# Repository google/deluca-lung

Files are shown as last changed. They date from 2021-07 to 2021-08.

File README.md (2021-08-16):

# deluca-lung

## Getting started
Instructions to provide to students: run the following commands
```
pip install deluca-lung
jupyter notebook
```

Navigate to the notebook `demo/2021-07-18 controller demo.ipynb` and run the cells.

## Setting up Raspberry Pi
- Create a Raspberry Pi OS image via [this](https://github.com/MinRegret/rpi-gadget-image-creator)

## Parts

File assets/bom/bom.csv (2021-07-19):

Category | Component | Quantity | Units / Package | $ / Package | # of Packages | Subtotal | Shipping | Tax | Total | Per Vent | Supplier | Link | Notes
Electronics | PCB for sensor / solenoid driver | 1 | 5 | $20.30 | 1 | $20.30 |  |  | $20.30 | $4.06 | JLCPCB | https://jlcpcb.com | https://github.com/MinRegret/deluca-lung/tree/main/assets/pcb/venti-zero
Electronics | Raspberry Pi Zero | 1 | 1 | $10.00 | 1 | $10.00 |  |  | $10.00 | $10.00 | Adafruit | https://www.adafruit.com/product/3400
Electronics | GPIO header | 1 | 1 | $0.95 | 1 | $0.95 |  |  | $0.95 | $0.95 | Adafruit | https://www.adafruit.com/product/2822
Electronics | GPIO ribbon | 1 | 1 | $2.50 | 1 | $2.50 |  |  | $2.50 | $2.50 | Mouser | https://www.mouser.com/ProductDetail/SparkFun/CAB-13028?qs=sGAEpiMZZMtyU1cDF2RqUE5bpLI3XpN5e3FkFOusz3o%3D
Electronics | 120W 24V Power Supply | 1 | 1 | $35.29 | 1 | $35.29 |  |  | $35.29 | $35.29 | Mouser | https://www.mouser.com/ProductDetail/709-RPS-120S-24
Electronics | 2-pin 5.08mm PCB screw terminal | 2 | 1 | $0.93 | 2 | $1.86 |  |  | $1.86 | $1.86 | Mouser | https://www.mouser.com/ProductDetail/571-2828372
Electronics | Female quick disconnct terminal | 3 | 1 | $0.30 | 3 | $0.90 |  |  | $0.90 | $0.90 | Mouser | https://www.mouser.com/ProductDetail/TE-Connectivity/3-520125-2?qs=%252BHUO%252BPuWh%2Fq0sCGvvzeevQ%3D%3D
Electronics | Pressure sensor | 1 | 1 | $42.00 | 1 | $42.00 |  |  | $42.00 | $42.00 | Mouser | https://www.mouser.com/ProductDetail/683-1PSI-D1-4V-MINI
Electronics | Flow sensor | 1 | 1 | $52.70 | 1 | $52.70 |  |  | $52.70 | $52.70 | Mouser | https://www.mouser.com/ProductDetail/683-5INCH-D2-P4VMINI
Electronics | MicroSD card | 1 | 1 | $7.99 | 1 | $7.99 |  |  | $7.99 | $7.99 | Mouser | https://www.mouser.com/ProductDetail/Parallax/32328?qs=%252BEew9%252B0nqrBvH%252BuscVQRmA%3D%3D
Electronics | 16 AWG wire | 0.5 | 200 | $16.95 | 1 | $16.95 |  |  | $16.95 | $0.04 | Amazon | https://www.amazon.com/GS-Power-Aluminum-Speaker-Amplifier/dp/B07584SQX5?s=electronics
Electronics | AC power inlet | 1 | 1 | $15.15 | 1 | $15.15 |  |  | $15.15 | $15.15 | McMaster | https://www.mcmaster.com/5428N114/
Electronics | Mini HDMI to HDMI extension cable | 1 | 1 | $17.50 | 1 | $17.50 |  |  | $17.50 | $17.50 | Amazon | https://www.amazon.com/gp/product/B075LH8K3W/ref=ppx_yo_dt_b_asin_title_o00_s00?ie=UTF8&th=1
Electronics | MicroSD extension cable | 1 | 1 | $5.99 | 1 | $5.99 |  |  | $5.99 | $5.99 | Amazon | https://www.amazon.com/gp/product/B07WWVBK8V/ref=ppx_yo_dt_b_search_asin_title?ie=UTF8&psc=1
Electronics | Micro USB extension cable | 1 | 2 | $5.99 | 1 | $5.99 |  |  | $5.99 | $3.00 | Amazon | https://www.amazon.com/gp/product/B07YDG6B6R/ref=ppx_yo_dt_b_asin_title_o00_s01?ie=UTF8&psc=1
Pneumatics | Inspiratory valve | 1 | 1 | $107.10 | 1 | $107.10 |  |  | $107.10 | $107.10 | SMC Pneumatics | https://www.smcpneumatics.com/PVQ31-5G-23-01N-H.html
Pneumatics | Expiratory valve | 1 | 1 | $58.80 | 1 | $58.80 |  |  | $58.80 | $58.80 | SMC Pneumatics | https://www.smcpneumatics.com/VXZ230EF.html
Pneumatics | Inspiratory right angle connector | 1 | 2 | $0.01 | 1 | $0.01 |  |  | $0.01 | $0.01 | TO PRINT | https://github.com/MinRegret/deluca-lung/blob/main/assets/stl/inspiratory-right-angle%20v4.stl
Pneumatics | Expiratory right angle connector | 1 | 2 | $0.01 | 1 | $0.01 |  |  | $0.01 | $0.01 | TO PRINT | https://github.com/MinRegret/deluca-lung/blob/main/assets/stl/expiratory-right-angle%20v5.stl
Pneumatics | Inspiratory tubing 5mm ID 8mm OD | 0.25 | 10 | $7.40 | 1 | $7.40 |  |  | $7.40 | $0.19 | McMaster | https://www.mcmaster.com/50315K71-50315K713/
Pneumatics | Expiratory tubing 8mm ID 12mm OD | 0.25 | 10 | $15.00 | 1 | $15.00 |  |  | $15.00 | $0.38 | McMaster | https://www.mcmaster.com/50315K73-50315K734/
Pneumatics | Gas sampling line connector I | 8 | 10 | $4.36 | 1 | $4.36 |  |  | $4.36 | $3.49 | McMaster | https://www.mcmaster.com/51525K121/
Pneumatics | Gas sampling line connector II | 1 | 10 | $4.84 | 1 | $4.84 |  |  | $4.84 | $0.48 | McMaster | https://www.mcmaster.com/51525K425
Pneumatics | Gas sampling line | 2 | 25 | $6.00 | 1 | $6.00 |  |  | $6.00 | $0.48 | McMaster | https://www.mcmaster.com/6516T11/
Pneumatics | Industrial quick-disconnect hose coupling | 1 | 1 | $4.58 | 1 | $4.58 |  |  | $4.58 | $4.58 | McMaster | https://www.mcmaster.com/4342K24/
Pneumatics | 50 PSI fixed-pressure compressed air regulator | 1 | 1 | $47.94 | 1 | $47.94 |  |  | $47.94 | $47.94 | McMaster | https://www.mcmaster.com/1777K1-1777K21/
Pneumatics | 1/8 x 1/8 NPT straight adapter | 1 | 1 | $1.68 | 1 | $1.68 |  |  | $1.68 | $1.68 | McMaster | https://www.mcmaster.com/4830K111/
Frame | Base | 1 | 1 | $5.00 | 1 | $5.00 |  |  | $5.00 | $5.00 | TO PRINT | https://github.com/MinRegret/deluca-lung/blob/main/assets/stl/Ventilator%20v36.stl
Frame | Shell | 1 | 1 | $5.00 | 1 | $5.00 |  |  | $5.00 | $5.00 | TO PRINT | https://github.com/MinRegret/deluca-lung/blob/main/assets/stl/Shell%20v14.stl
Fasteners | M3 thin hex nut | 6 | 100 | $3.66 | 1 | $3.66 |  |  | $3.66 | $0.22 | McMaster | https://www.mcmaster.com/90695A033/
Fasteners | M3x0.5mm 22mm FHCS | 2 | 50 | $7.30 | 1 | $7.30 |  |  | $7.30 | $0.29 | McMaster | https://www.mcmaster.com/91294A137/
Fasteners | M3x0.5mm 35mm SHCS | 2 | 50 | $11.03 | 1 | $11.03 |  |  | $11.03 | $0.44 | McMaster | https://www.mcmaster.com/91290A135/
Fasteners | M4x0.7mm 20mm SHCS | 3 | 100 | $9.57 | 1 | $9.57 |  |  | $9.57 | $0.29 | McMaster | https://www.mcmaster.com/90128A216/
Fasteners | M4x0.7mm 35mm SHCS | 4 | 50 | $7.79 | 1 | $7.79 |  |  | $7.79 | $0.62 | McMaster | https://www.mcmaster.com/91292A131/
Fasteners | M2.5 inserts | 8 | 100 | $11.19 | 1 | $11.19 |  |  | $11.19 | $0.90 | McMaster | https://www.mcmaster.com/94180A321/
Fasteners | M3 inserts | 4 | 100 | $13.35 | 1 | $13.35 |  |  | $13.35 | $0.53 | McMaster | https://www.mcmaster.com/94180A331
Fasteners | M4 inserts | 4 | 50 | $9.37 | 1 | $9.37 |  |  | $9.37 | $0.75 | McMaster | https://www.mcmaster.com/94180A353/
Fasteners | M3x0.5mm 8mm SHCS | 4 | 100 | $7.88 | 1 | $7.88 |  |  | $7.88 | $0.32 | McMaster | https://www.mcmaster.com/91290A113/
Fasteners | M2.5x0.45mm 6mm SHCS | 8 | 50 | $9.51 | 1 | $9.51 |  |  | $9.51 | $1.52 | McMaster | https://www.mcmaster.com/91290A101/
Fasteners | M3 0.45mm OD 3mm spacers | 4 | 1 | $1.23 | 4 | $4.92 |  |  | $4.92 | $4.92 | McMaster | https://www.mcmaster.com/93657A203/
Fasteners | M2.5 0.45mm OD 2mm spacers | 8 | 1 | $1.20 | 8 | $9.60 |  |  | $9.60 | $9.60 | McMaster | https://www.mcmaster.com/93657A200/
Consumables | DAR large electrostatic filter | 2 | 50 | $65.73 | 1 | $65.73 |  |  | $65.73 | $2.63 | TigerMedical | https://www.tigermedical.com/Products/DAR-Electrostatic-Filter__COV350U5865__COV350U5879-.aspx?invsrc=adwords_tm
Consumables | PEEP valve | 1 | 1 | $7.26 | 1 | $7.26 |  |  | $7.26 | $7.26 | SaveRiteMedical | https://www.saveritemedical.com/products/airlife-adjustable-peep-valves-with-22mm-i-d-connection-and-22mm-adapter
Consumables | One-way valve | 1 | 1 | $1.58 | 1 | $1.58 |  |  | $1.58 | $1.58 | SaveRiteMedical | https://www.saveritemedical.com/products/one-way-valve-22mm-id-od-connections
Consumables | Respiratory circuit | 1 | 1 | $13.00 | 1 | $13.00 |  |  | $13.00 | $13.00 | ORSupply | https://orsupply.com/product/1505

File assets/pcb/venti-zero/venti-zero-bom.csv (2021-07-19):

Designator | Manufacturer | Footprint | LCSC Part Number | Comment
J1 | JILN | HDR-TH_40P-P2.54-V | C429953 | https://lcsc.com/product-detail/Pin-Header-Female-Header_JILN-22850140ANG1SYA01_C429953.html/?href=jlc-SMT
J2 | Phoenix Contact | CONN-TH_P5.08_1715721 | C480516 | https://lcsc.com/product-detail/Screw-terminal_Phoenix-Contact-1715721_C480516.html/?href=jlc-SMT
J3 | Phoenix Contact | CONN-TH_P5.08_1715721 | C480516 | https://lcsc.com/product-detail/Screw-terminal_Phoenix-Contact-1715721_C480516.html/?href=jlc-SMT
J4 | Phoenix Contact | CONN-TH_P5.08_1715721 | C480516 | https://lcsc.com/product-detail/Screw-terminal_Phoenix-Contact-1715721_C480516.html/?href=jlc-SMT
U2 | Texas Instruments | MSOP-10_3.0x3.0x0.5P | C37593 | https://lcsc.com/product-detail/Analog-To-Digital-Converters-ADCs_TI_ADS1115IDGSR_ADS1115IDGSR_C37593.html/?href=jlc-SMT
U4 | Texas Instruments | SOIC-16_3.9x9.9x1.27P | C7512 | https://lcsc.com/product-detail/Darlington-transistor-array-driver_Texas-Instruments_ULN2003ADR_Texas-Instruments-TI-ULN2003ADR_C7512.html/?href=jlc-SMT

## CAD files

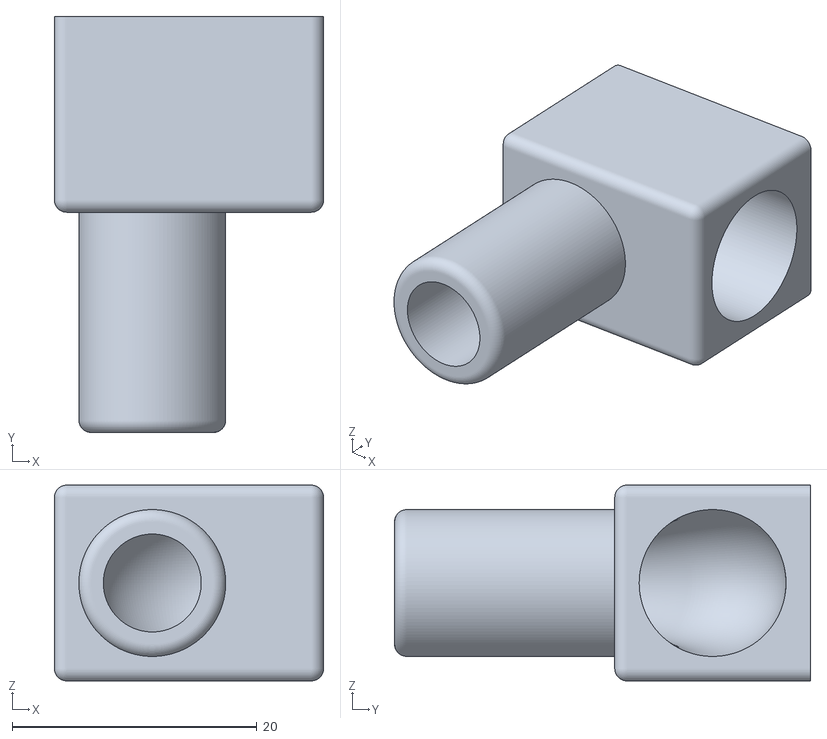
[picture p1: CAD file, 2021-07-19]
assets/stl/expiratory-right-angle v5.stl
22.0 x 34.0 x 16.0

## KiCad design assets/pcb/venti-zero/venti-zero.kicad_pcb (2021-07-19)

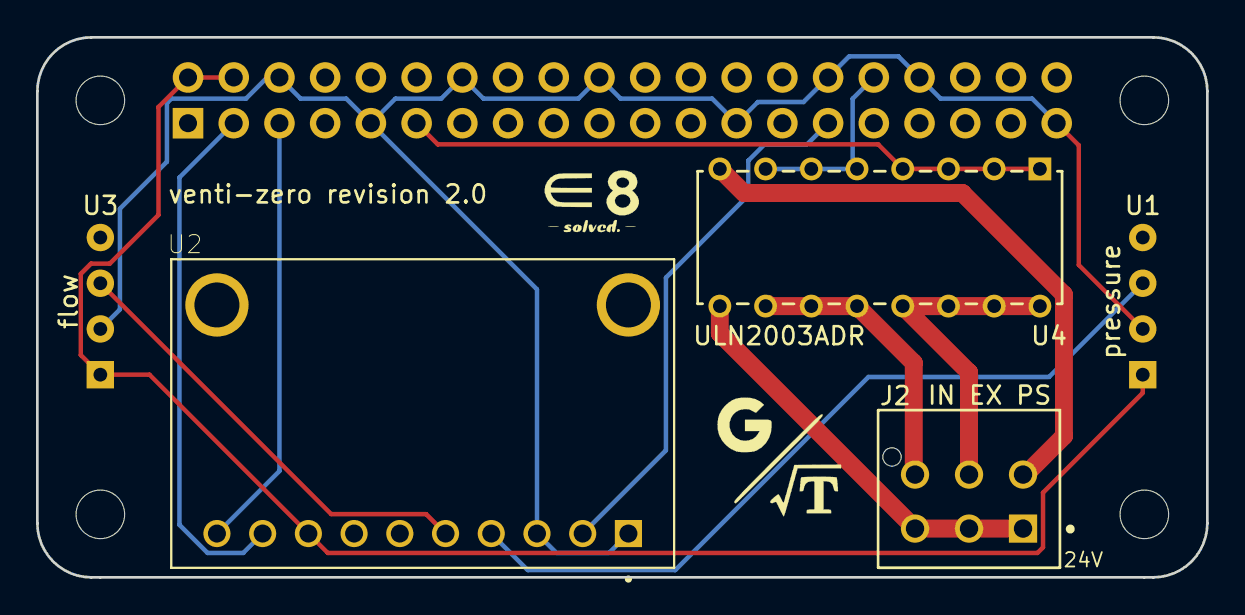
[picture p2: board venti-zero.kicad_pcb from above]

Board: 2 copper layers, 65.0 x 30.0 mm, 10 parts (1 on the bottom side), 13 nets.

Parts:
H1, H2, H3, H4: MountingHole; MountingHole_2.7mm_M2.5_uHAT_RPi
J1: GPIO_CONNECTOR; PinSocket_2x20_P2.54mm_Vertical_Centered_Anchor
J2: 206832-0601; Molex-206832-0601-MFG
U1: pressure; MINI-P-Sensor-Horizontal
U2: ADS1115IDGSR; ADS1115
U3: flow; MINI-P-Sensor-Horizontal
U4: ULN2003ADR; ULN2003A

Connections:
+5V: J1.2, J1.4, U1.1, U2.8, U3.1
+24V: J2.1, J2.3, J2.5, U4.9
/GPIO2_SDA1: J1.3, U2.9
/GPIO3_SCL1: J1.5, U2.10
/GPIO5: J1.29, U2.2
/GPIO12: J1.32, U4.5, U4.6, U4.7
/GPIO17: J1.11, U4.1, U4.2, U4.3, U4.4
GND: J1.6, J1.9, J1.14, J1.20, J1.25, J1.30, J1.34, J1.39, U1.2, U2.1, U2.3, U3.2
GND1: J2.2, U4.8
unnamed: J2.4, U4.13, U4.14, U4.15, U4.16
unnamed: J2.6, U4.10, U4.11, U4.12
unnamed: U1.3, U2.4
unnamed: U2.5, U3.3

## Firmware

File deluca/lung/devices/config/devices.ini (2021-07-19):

[gpio]
type = PigpioConnection
module = devices
host = "10.55.0.1"
port = 8888
show_errors = False

[adc]
type   = ADS1015
module = devices
address = 0x48
i2c_bus = 1

[control_valve]
# SMC PVQ-31-5G-23-01N Proportional Valve
type     = PWMControlValve
module   = devices.valves
pin      = 12
form     = "Normally Closed"
response = "deluca/lung/devices/config/calibration/SMC_PVQ31_5G_23_01N_response"

[expiratory_valve]
# The big-boy NC valve from SMC
type    = OnOffValve
module  = devices.valves
pin     = 17
form    = "Normally Closed"

[pressure_sensor]
# Note: calibration must convert to units cm(h20)

# The following config is for an Amphenol/All Sensors 20 INCH-G-P4V-MINI
# Datasheet: https://www.mouser.com/datasheet/2/18/DS-0102_Rev_A-1499183.pdf
#  FIXME: It may be valuable/necessary to specify per-sensor acceptable drift in this file.
#  FIXME: See note in io.devices.sensors.AnalogSensor._verify()
type              = AnalogSensor
module            = devices.sensors
adc               = adc
MUX               = 0
offset_voltage    = 2.25
output_span       = 2.0
conversion_factor = 70.3

[flow_sensor_ex]
# Experimental! 5 INCH-D-P4V-MINI hooked up to a D-LITE
type              = DLiteSensor
module            = devices.sensors
adc               = adc
MUX               = 1
offset_voltage    = 2.25
output_span       = 4.0
conversion_factor = 1

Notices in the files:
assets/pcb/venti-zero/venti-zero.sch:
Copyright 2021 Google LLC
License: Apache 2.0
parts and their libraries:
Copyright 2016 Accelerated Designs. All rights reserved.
